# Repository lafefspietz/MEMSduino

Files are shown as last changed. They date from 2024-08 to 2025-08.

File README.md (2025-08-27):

# [MEMSduino: Arduino-Based Controller for MEMS Switches](https://github.com/lafefspietz/MEMSduino/)

## [files.html](files.html)

## [NIST Tech note describing system](https://doi.org/10.6028/NIST.TN.2335)
## [Video demonstrating operation, Zenodo.org page](https://zenodo.org/records/14811301)
## [Video doi at Zenodo](https://doi.org/10.5281/zenodo.14811300)

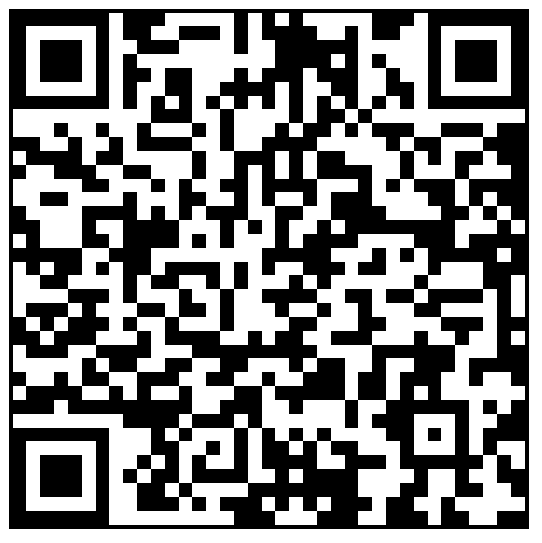
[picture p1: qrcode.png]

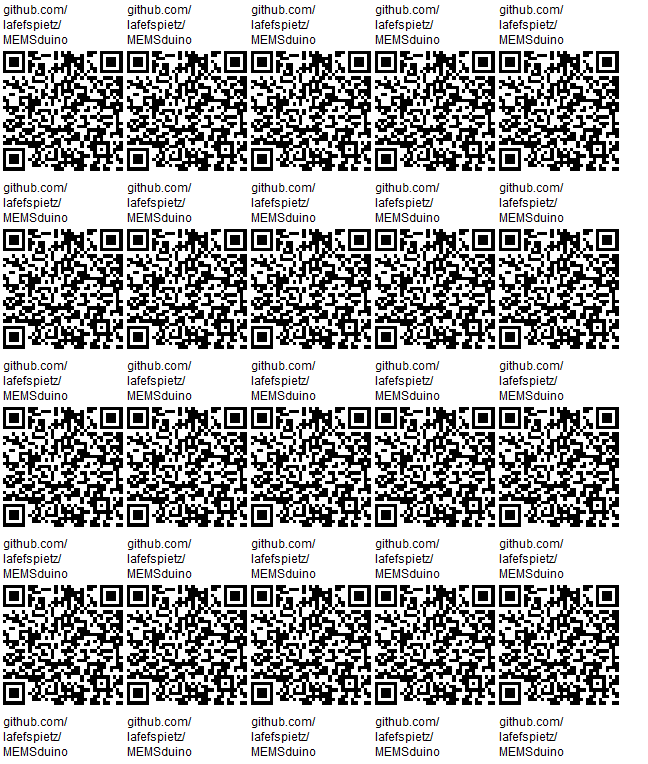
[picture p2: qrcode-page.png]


Open source system for controlling MEMS switches using an Arduino.  This system allows for both serial control via software and physical control by a human operator with buttons and indicator lights of a range of possible MEMS switch configurations.  A set of relays are controlled by the Arduino, which determines which of the lines on a DSUB connector are energized with a 90 volt signal.  This DSUB can then be connected to any cryogenic wiring which leads to the various DC control lines of a cryogenic MEMS RF switch.  

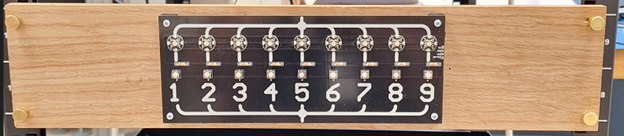
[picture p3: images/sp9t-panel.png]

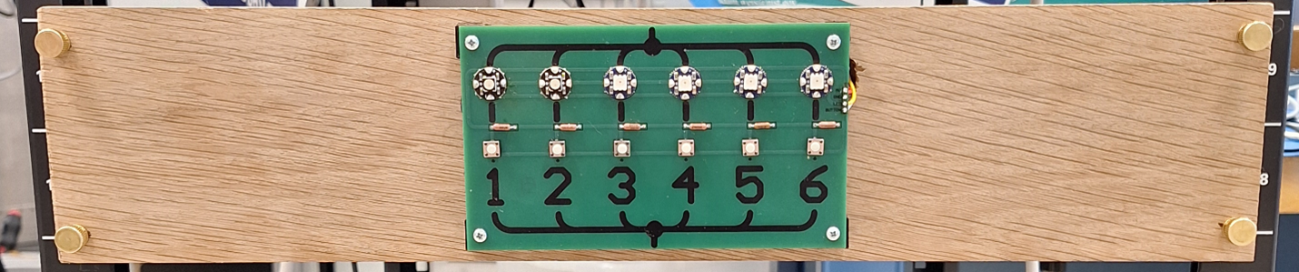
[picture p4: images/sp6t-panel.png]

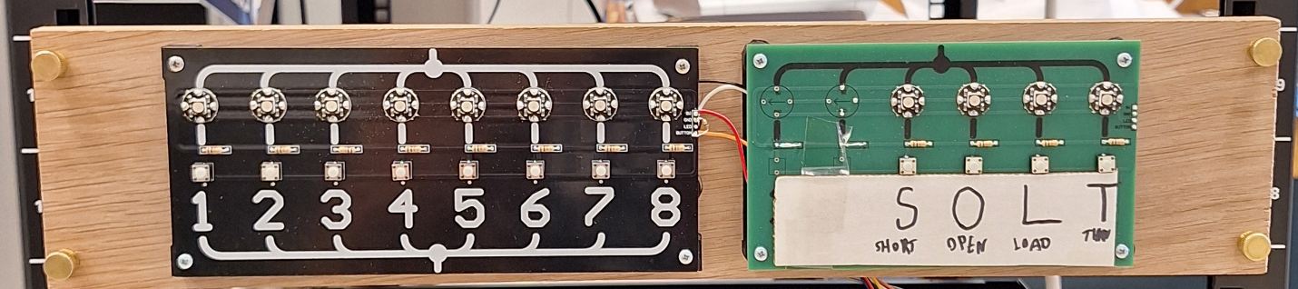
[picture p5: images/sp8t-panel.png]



## Python Code Snippets

List com port objects:
```
import serial
import serial.tools.list_ports
ports = serial.tools.list_ports.comports()

for port, desc, hwid in sorted(ports):
       print("{}: {} [{}]".format(port, desc, hwid))

```

Create serial object
```
SP9T_serial = serial.Serial('COM18', 9600)  # open serial port

```

Write to set to port 2:

```
SP9T_serial.write(bytes(str(2), encoding='utf-8'))

```

## [SP6T-COTS/](SP6T-COTS/)

## [DUAL-SP3T-COTS/](DUAL-SP3T-COTS/)

## [SP9T/](SP9T/)

## [DUAL-SP3T-COTS-SINGLE-DCDC/](DUAL-SP3T-COTS-SINGLE-DCDC/)

## [METAL BOX](metal-box/)

## [arXiv preprint DOI](https://arxiv.org/abs/2501.03340)

## All Files

 - [6_port_controller.ino](https://github.com/lafefspietz/MEMSduino/raw/refs/heads/main/6_port_controller.ino)
 - [6button-6eopixel.SchDoc](https://github.com/lafefspietz/MEMSduino/raw/refs/heads/main/6button-6eopixel.SchDoc)
 - [6button-6neopixel-BOM.xlsx](https://github.com/lafefspietz/MEMSduino/raw/refs/heads/main/6button-6neopixel-BOM.xlsx)
 - [6button-6neopixel-gerbers.zip](https://github.com/lafefspietz/MEMSduino/raw/refs/heads/main/6button-6neopixel-gerbers.zip)
 - [6button-6neopixel.PcbDoc](https://github.com/lafefspietz/MEMSduino/raw/refs/heads/main/6button-6neopixel.PcbDoc)
 - [6button-6neopixels.PrjPcb](https://github.com/lafefspietz/MEMSduino/raw/refs/heads/main/6button-6neopixels.PrjPcb)
 - [6button-6neopixels.PrjPcbStructure](https://github.com/lafefspietz/MEMSduino/raw/refs/heads/main/6button-6neopixels.PrjPcbStructure)
 - [9-port-controller.ino](https://github.com/lafefspietz/MEMSduino/raw/refs/heads/main/9-port-controller.ino)
 - [9button-9neopixel-BOM.xlsx](https://github.com/lafefspietz/MEMSduino/raw/refs/heads/main/9button-9neopixel-BOM.xlsx)
 - [9button-9neopixel-gerbers.zip](https://github.com/lafefspietz/MEMSduino/raw/refs/heads/main/9button-9neopixel-gerbers.zip)
 - [9button-9neopixel.PcbDoc](https://github.com/lafefspietz/MEMSduino/raw/refs/heads/main/9button-9neopixel.PcbDoc)
 - [9button-9neopixel.SchDoc](https://github.com/lafefspietz/MEMSduino/raw/refs/heads/main/9button-9neopixel.SchDoc)
 - [9button-9neopixels.PrjPcb](https://github.com/lafefspietz/MEMSduino/raw/refs/heads/main/9button-9neopixels.PrjPcb)
 - [9button-9neopixels.PrjPcbStructure](https://github.com/lafefspietz/MEMSduino/raw/refs/heads/main/9button-9neopixels.PrjPcbStructure)
 - [AN-1304-A-box-modifications.SLDDRW](https://github.com/lafefspietz/MEMSduino/raw/refs/heads/main/AN-1304-A-box-modifications.SLDDRW)
 - [AN-1304-A-box-modifications.SLDPRT](https://github.com/lafefspietz/MEMSduino/raw/refs/heads/main/AN-1304-A-box-modifications.SLDPRT)
 - [AN-1304-A-box-modifications.STEP](https://github.com/lafefspietz/MEMSduino/raw/refs/heads/main/AN-1304-A-box-modifications.STEP)
 - [AN-1304-A-box-modifications.pdf](https://github.com/lafefspietz/MEMSduino/raw/refs/heads/main/AN-1304-A-box-modifications.pdf)
 - [AN-1304-A-lid-modifications.SLDDRW](https://github.com/lafefspietz/MEMSduino/raw/refs/heads/main/AN-1304-A-lid-modifications.SLDDRW)
 - [AN-1304-A-lid-modifications.SLDPRT](https://github.com/lafefspietz/MEMSduino/raw/refs/heads/main/AN-1304-A-lid-modifications.SLDPRT)
 - [AN-1304-A-lid-modifications.STEP](https://github.com/lafefspietz/MEMSduino/raw/refs/heads/main/AN-1304-A-lid-modifications.STEP)
 - [AN-1304-A-lid-modifications.pdf](https://github.com/lafefspietz/MEMSduino/raw/refs/heads/main/AN-1304-A-lid-modifications.pdf)
 - [DB25-relay-HV-control-BOM.xlsx](https://github.com/lafefspietz/MEMSduino/raw/refs/heads/main/DB25-relay-HV-control-BOM.xlsx)
 - [DB25-relay-HV-control-gerbers.zip](https://github.com/lafefspietz/MEMSduino/raw/refs/heads/main/DB25-relay-HV-control-gerbers.zip)
 - [DB25-relay-HV-control.PcbDoc](https://github.com/lafefspietz/MEMSduino/raw/refs/heads/main/DB25-relay-HV-control.PcbDoc)
 - [DB25-relay-HV-control.PrjPcb](https://github.com/lafefspietz/MEMSduino/raw/refs/heads/main/DB25-relay-HV-control.PrjPcb)
 - [DB25-relay-HV-control.PrjPcbStructure](https://github.com/lafefspietz/MEMSduino/raw/refs/heads/main/DB25-relay-HV-control.PrjPcbStructure)
 - [DB25-relay-HV-control.SchDoc](https://github.com/lafefspietz/MEMSduino/raw/refs/heads/main/DB25-relay-HV-control.SchDoc)
 - [HV-DCDC-bracket.SLDDRW](https://github.com/lafefspietz/MEMSduino/raw/refs/heads/main/HV-DCDC-bracket.SLDDRW)
 - [HV-DCDC-bracket.SLDPRT](https://github.com/lafefspietz/MEMSduino/raw/refs/heads/main/HV-DCDC-bracket.SLDPRT)
 - [HV-DCDC-bracket.STL](https://github.com/lafefspietz/MEMSduino/raw/refs/heads/main/HV-DCDC-bracket.STL)
 - [HV-DCDC-bracket.pdf](https://github.com/lafefspietz/MEMSduino/raw/refs/heads/main/HV-DCDC-bracket.pdf)
 - [SP6T-COTS-BOM.xlsx](https://github.com/lafefspietz/MEMSduino/raw/refs/heads/main/SP6T-COTS-BOM.xlsx)
 - [SP9T-Custom-BOM.xlsx](https://github.com/lafefspietz/MEMSduino/raw/refs/heads/main/SP9T-Custom-BOM.xlsx)
 - [arduino-bracket.SLDDRW](https://github.com/lafefspietz/MEMSduino/raw/refs/heads/main/arduino-bracket.SLDDRW)
 - [arduino-bracket.SLDPRT](https://github.com/lafefspietz/MEMSduino/raw/refs/heads/main/arduino-bracket.SLDPRT)
 - [arduino-bracket.STL](https://github.com/lafefspietz/MEMSduino/raw/refs/heads/main/arduino-bracket.STL)
 - [arduino-bracket.pdf](https://github.com/lafefspietz/MEMSduino/raw/refs/heads/main/arduino-bracket.pdf)
 - [arduino-to-headers-shield-BOM.xlsx](https://github.com/lafefspietz/MEMSduino/raw/refs/heads/main/arduino-to-headers-shield-BOM.xlsx)
 - [arduino-to-headers-shield-gerbers.zip](https://github.com/lafefspietz/MEMSduino/raw/refs/heads/main/arduino-to-headers-shield-gerbers.zip)
 - [arduino-to-headers-shield.PcbDoc](https://github.com/lafefspietz/MEMSduino/raw/refs/heads/main/arduino-to-headers-shield.PcbDoc)
 - [arduino-to-headers-shield.PrjPcb](https://github.com/lafefspietz/MEMSduino/raw/refs/heads/main/arduino-to-headers-shield.PrjPcb)
 - [arduino-to-headers-shield.PrjPcbStructure](https://github.com/lafefspietz/MEMSduino/raw/refs/heads/main/arduino-to-headers-shield.PrjPcbStructure)
 - [arduino-to-headers-shield.SchDoc](https://github.com/lafefspietz/MEMSduino/raw/refs/heads/main/arduino-to-headers-shield.SchDoc)
 - [cryoelec-bracket.SLDDRW](https://github.com/lafefspietz/MEMSduino/raw/refs/heads/main/cryoelec-bracket.SLDDRW)
 - [cryoelec-bracket.SLDPRT](https://github.com/lafefspietz/MEMSduino/raw/refs/heads/main/cryoelec-bracket.SLDPRT)
 - [cryoelec-bracket.STL](https://github.com/lafefspietz/MEMSduino/raw/refs/heads/main/cryoelec-bracket.STL)
 - [cryoelec-bracket.pdf](https://github.com/lafefspietz/MEMSduino/raw/refs/heads/main/cryoelec-bracket.pdf)
 - [front-panel-center-bracket.SLDDRW](https://github.com/lafefspietz/MEMSduino/raw/refs/heads/main/front-panel-center-bracket.SLDDRW)
 - [front-panel-center-bracket.SLDPRT](https://github.com/lafefspietz/MEMSduino/raw/refs/heads/main/front-panel-center-bracket.SLDPRT)
 - [front-panel-center-bracket.STL](https://github.com/lafefspietz/MEMSduino/raw/refs/heads/main/front-panel-center-bracket.STL)
 - [front-panel-center-bracket.pdf](https://github.com/lafefspietz/MEMSduino/raw/refs/heads/main/front-panel-center-bracket.pdf)
 - [front-panel-edge-bracket.SLDDRW](https://github.com/lafefspietz/MEMSduino/raw/refs/heads/main/front-panel-edge-bracket.SLDDRW)
 - [front-panel-edge-bracket.SLDPRT](https://github.com/lafefspietz/MEMSduino/raw/refs/heads/main/front-panel-edge-bracket.SLDPRT)
 - [front-panel-edge-bracket.STL](https://github.com/lafefspietz/MEMSduino/raw/refs/heads/main/front-panel-edge-bracket.STL)
 - [front-panel-edge-bracket.pdf](https://github.com/lafefspietz/MEMSduino/raw/refs/heads/main/front-panel-edge-bracket.pdf)
 - [rack-mount-board-SP6T.SLDDRW](https://github.com/lafefspietz/MEMSduino/raw/refs/heads/main/rack-mount-board-SP6T.SLDDRW)
 - [rack-mount-board-SP6T.SLDPRT](https://github.com/lafefspietz/MEMSduino/raw/refs/heads/main/rack-mount-board-SP6T.SLDPRT)
 - [rack-mount-board-SP6T.pdf](https://github.com/lafefspietz/MEMSduino/raw/refs/heads/main/rack-mount-board-SP6T.pdf)
 - [rack-mount-board-SP9T.SLDDRW](https://github.com/lafefspietz/MEMSduino/raw/refs/heads/main/rack-mount-board-SP9T.SLDDRW)
 - [rack-mount-board-SP9T.SLDPRT](https://github.com/lafefspietz/MEMSduino/raw/refs/heads/main/rack-mount-board-SP9T.SLDPRT)
 - [rack-mount-board-SP9T.pdf](https://github.com/lafefspietz/MEMSduino/raw/refs/heads/main/rack-mount-board-SP9T.pdf)
 - [switch_control_matlab.m](https://github.com/lafefspietz/MEMSduino/raw/refs/heads/main/switch_control_matlab.m)
 - [switch_control_python.py](https://github.com/lafefspietz/MEMSduino/raw/refs/heads/main/switch_control_python.py)

## SP6T BOM

 - [1/2" White oak board, 4" x 24"](https://ocoochhardwoods.com/detail/?i=124wo)
 - [Brass Flared-Collar Knurled-Head Thumb Screws 10-32 Thread Size, 3/4" Long](https://www.mcmaster.com/92421A645/)
 - [#6 wood screws](https://www.amazon.com/Stainless-Phillips-Screws-Multipurpose-TPOHH/dp/B0CHRWGT8N)
 - [cryoelec-bracket](https://github.com/lafefspietz/MEMSduino/raw/refs/heads/main/cryoelec-bracket.STL)
 - [arduino-bracket](https://github.com/lafefspietz/MEMSduino/raw/refs/heads/main/arduino-bracket.STL)
 - [front-panel-edge-bracket](https://github.com/lafefspietz/MEMSduino/raw/refs/heads/main/front-panel-edge-bracket.STL)
 - [Brass threaded inserts #4-40](https://www.3djake.com/ruthex/threaded-insert-4-40-unc-100-pieces)
 - [0-80 Brass Thread Inserts(E-Z LOK 240-000-BR)](https://www.amazon.com/Z-LOK-Threaded-Insert-Plastic/dp/B08QJJDCW1/)
 - [0-80 screws  3/16" phillips, stainless](https://www.amazon.com/Machine-Screws-Phillips-Stainless-Steel/dp/B07X8NTTB9/)
 - [Zinc-Plated Steel Pan Head Phillips Screw 4-40 Thread, 1/4" Long](https://www.mcmaster.com/90272A106/)
 - [Diecast aluminum enclosure, AN-1304-A from BUD Industries](https://www.digikey.com/en/products/detail/bud-industries/AN-1304-A/5804538)
 - [Male-Female Threaded Hex Standoff 18-8 Stainless Steel, 3/16" Hex, 7/32" Long, 4-40 to 4-40 Thread](https://www.mcmaster.com/91075A462/)
 - [Brass Socket Head Screw 4-40 Thread Size, 3/4" Long](https://www.mcmaster.com/93465A113/ )
 - [Brass Washer for Number 4 Screw Size, 0.12" ID, 0.281" OD](https://www.mcmaster.com/92916A320/)
 - [6button-6neopixel, 152.4 mm x 88.9 mm (6""x3.5")](https://github.com/lafefspietz/MEMSduino/raw/refs/heads/main/6button-6neopixel-gerbers.zip)
 - [arduino-to-headers-shield 53.34 mm x 70.78 mm (2.1" x 2.79")](https://github.com/lafefspietz/MEMSduino/raw/refs/heads/main/arduino-to-headers-shield-gerbers.zip)
 - [100k axial resistor](https://www.digikey.com/en/products/detail/stackpole-electronics-inc/RNF14FTD100K/1706591)
 - [10k axial resistor](https://www.digikey.com/en/products/detail/yageo/MFR-25FBF52-10K/13219)
 - [330 ohm axial resistor](https://www.digikey.com/en/products/detail/stackpole-electronics-inc/CF18JT330R/1741683)
 - [1000 uF electrolytic capacitor](https://www.digikey.com/en/products/detail/rubycon/16PK1000MEFC10X12-5/3563556)
 - [Momentary buttons](https://www.digikey.com/en/products/detail/e-switch/TL59NF160Q/390533)
 - [JUMPER WIRE M/M 6" 20PCS](https://www.digikey.com/en/products/detail/sparkfun-electronics/PRT-12795/5993860)
 - [DB25 panel mount solder cup](https://www.digikey.com/en/products/detail/norcomp-inc/171-025-203L001/858144)
 - [Arduino UNO](https://www.digikey.com/en/products/detail/dfrobot/DFR0216/6579366)
 - [USB A to USB B cable](https://www.digikey.com/en/products/detail/assmann-wsw-components/AK672-2-2/947492)
 - [Neopixel programmable RGB LED](https://www.adafruit.com/product/1559)
 - [2 wire header cable](https://www.amazon.com/ZYAMY-Dupont-Connector-Multicolor-Breadboard/dp/B0B8Z23NWX/)
 - [4 wire header cable](https://www.amazon.com/ZYAMY-Dupont-Connector-Multicolor-Breadboard/dp/B0789F523N/)
 - [8 wire header cable](https://www.amazon.com/ZYAMY-Dupont-Connector-Multicolor-Breadboard/dp/B0789F2Y1T/ )
 - [0.1" headers](https://www.amazon.com/Header-Lystaii-Pin-Connector-Electronic/dp/B06ZZN8L9S/)

## SP9T Build BOM

 - [1/2" White oak board, 4" x 24"](https://ocoochhardwoods.com/detail/?i=124wo)
 - [Brass Flared-Collar Knurled-Head Thumb Screws 10-32 Thread Size, 3/4"" Long](https://www.mcmaster.com/92421A645/)
 - [#6 wood screws](https://www.amazon.com/Stainless-Phillips-Screws-Multipurpose-TPOHH/dp/B0CHRWGT8N)
 - [HV-DCDC-bracket.STL 3d print(4 g of filament, 14 minutes print time)](https://github.com/lafefspietz/MEMSduino/raw/refs/heads/main/HV-DCDC-bracket.STL)
 - [arduino-bracket.STL 3d print(4 g of filament, 17 minutes print time)](https://github.com/lafefspietz/MEMSduino/raw/refs/heads/main/arduino-bracket.STL)
 - [front-panel-edge-bracket.STL 3d print (3 g of filament, 14 minutes print time)](https://github.com/lafefspietz/MEMSduino/raw/refs/heads/main/front-panel-edge-bracket.STL)
 - [front-panel-center-bracket 3d print (1 g of filament, 7 minutes print time)](https://github.com/lafefspietz/MEMSduino/raw/refs/heads/main/front-panel-center-bracket.STL)
 - [Brass threaded inserts #4-40](https://www.3djake.com/ruthex/threaded-insert-4-40-unc-100-pieces)
 - [Zinc-Plated Steel Pan Head Phillips Screw 4-40 Thread, 1/4" Long](https://www.mcmaster.com/90272A106/)
 - [Diecast aluminum enclosure, AN-1304-A from BUD Industries](https://www.digikey.com/en/products/detail/bud-industries/AN-1304-A/5804538)
 - [Male-Female Threaded Hex Standoff 18-8 Stainless Steel, 3/16" Hex, 7/32" Long, 4-40 to 4-40 Thread](https://www.mcmaster.com/91075A462/)
 - [Brass Socket Head Screw 4-40 Thread Size, 3/4"" Long"](https://www.mcmaster.com/93465A113/ )
 - [Brass Washer for Number 4 Screw Size, 0.12" ID, 0.281" OD](https://www.mcmaster.com/92916A320/)
 - [5V-12V boost](https://www.amazon.com/KUNCAN-Converter-Cable-Voltage-Connector/dp/B01ID90K4A/?th=1)
 - [12V to HV boost](https://www.amazon.com/Voltage-Converter-Vintage-Indicator-80V-380V/dp/B09D93QNYK)
 - [heat shrink tubing](https://www.digikey.com/en/products/detail/3m/SFTW203-1-16-BL-SPL/22044171)
 - [9button-9neopixel 228.6mm x 88.9mm (9" x 3.5") printed circuit board](https://github.com/lafefspietz/MEMSduino/raw/refs/heads/main/9button-9neopixel-gerbers.zip)
 - [arduino-to-headers-shield 53.34 mm x 70.78 mm (2.1" x 2.79") printed circuit board](https://github.com/lafefspietz/MEMSduino/raw/refs/heads/main/arduino-to-headers-shield-gerbers.zip)
 - [DB25-relay-HV-control 78.74 mm x 71.12 mm (3.1"x2.8") printed circuit board](https://github.com/lafefspietz/MEMSduino/raw/refs/heads/main/DB25-relay-HV-control-gerbers.zip)
 - [100k axial resistor](https://www.digikey.com/en/products/detail/stackpole-electronics-inc/RNF14FTD100K/1706591)
 - [10k axial resistor](https://www.digikey.com/en/products/detail/yageo/MFR-25FBF52-10K/13219)
 - [330 ohm axial resistor](https://www.digikey.com/en/products/detail/stackpole-electronics-inc/CF18JT330R/1741683)
 - [1000 uF electrolytic capacitor](https://www.digikey.com/en/products/detail/rubycon/16PK1000MEFC10X12-5/3563556)
 - [Momentary buttons](https://www.digikey.com/en/products/detail/e-switch/TL59NF160Q/390533)
 - [1 Mohm 1206 SMT resistor 1%](https://www.digikey.com/en/products/detail/yageo/RC1206FR-071ML/728388)
 - [DB25 board mount connector](https://www.digikey.com/en/products/detail/assmann-wsw-components/A-DF-25-PP-Z/1241794)
 - [RELAY REED SIP SPST .5A 5V W/DIO](https://www.digikey.com/en/products/detail/comus-international/3570-1331-053/7497099)
 - [Arduino UNO](https://www.digikey.com/en/products/detail/dfrobot/DFR0216/6579366)
 - [USB A to USB B cable](https://www.digikey.com/en/products/detail/assmann-wsw-components/AK672-2-2/947492)
 - [Neopixel programmable RGB LED](https://www.adafruit.com/product/1559)
 - [2 wire header cable](https://www.amazon.com/ZYAMY-Dupont-Connector-Multicolor-Breadboard/dp/B0B8Z23NWX/)
 - [4 wire header cable](https://www.amazon.com/ZYAMY-Dupont-Connector-Multicolor-Breadboard/dp/B0789F523N/)
 - [8 wire header cable](https://www.amazon.com/ZYAMY-Dupont-Connector-Multicolor-Breadboard/dp/B0789F2Y1T/ )
 - [0.1" headers](https://www.amazon.com/Header-Lystaii-Pin-Connector-Electronic/dp/B06ZZN8L9S/)

## Disclaimer

Certain equipment, instruments, software, or materials are identified in this document in order to specify the experimental procedure adequately.  Such identification is not intended to imply recommendation or endorsement of any product or service by NIST, nor is it intended to imply that the materials or equipment identified are necessarily the best available for the purpose.

## MEMSduino SP9T Build Sequence

1. Cut wood board and drill holes in it
2. Cut out holes and D Sub Cutout in BUD box, mount DSUB into D cutout with 4-40 standoffs, mount to wood with long 4-40 screws
3. 3d print all 3d printed parts and add heat-pressed thread inserts
4. Screw all brackets to the wood board except for the HV-DCDC-bracket.STL, which is screwed to the inside of the BUD box.
5. Assemble Arduino UNO Shield board (arduino-to-headers-shield)
6. Mount the Arduino UNO to the 3d printed Arduino mounting bracket with 4-40 screws and plug the shield into the UNO
6. Assemble Relay control board (DB25-relay-HV-control), solder to captive DSUB connector in the lid of BUD box
7. Assemble the DC DC converter as needed to get to 90 volts or install an off the shelf converter in the BUD box, mount the board to the board mount bracket.
8. Assemble front panel control circuit board, mount it to the plastic brackets on the wood board
9. Connect all the cables, test system

## MEMSduino SP6T COTS Build Sequence

1. Cut wood board and drill holes in it
2. Cut out holes and D Sub Cutout in BUD box, mount DSUB into D cutout with 4-40 standoffs, mount to wood with long 4-40 screws
3. 3d print all 3d printed parts and add heat-pressed thread inserts, 4-40 on all but cryoelec-bracket, which takes 0-80 thread inserts
4. Screw all brackets to the wood board except for the cryoelec-bracket.STL part, which is screwed to the inside of the BUD box with 4-40 screws
5. Assemble Arduino UNO Shield board (arduino-to-headers-shield)
6. Mount the Arduino UNO to the 3d printed Arduino mounting bracket with 4-40 screws and plug the shield into the UNO
7. Put male header pins in the input side of the DC DC converter, and the jumper wires in the output side, mount board in metal box with 0-80 screws, connect to the Arduino shield with one 8 wire cable and one 4 wire cable, making sure all pins map in order.
8. Solder the ends of the jumper wires into the solder cups in the DSUB connector, matching with whatever pins map to the appropriate pins on the cryogenic SP6T COTS switch
8. Assemble front panel control circuit board, mount it to the plastic brackets on the wood board
9. Connect all the cables, test system

## License

This data/work was created by employees of the National Institute of Standards and Technology (NIST), an agency of the Federal Government. Pursuant to title 17 United States Code Section 105, works of NIST employees are not subject to copyright protection in the United States.  This data/work may be subject to foreign copyright.

The data/work is provided by NIST as a public service and is expressly provided “AS IS.” NIST MAKES NO WARRANTY OF ANY KIND, EXPRESS, IMPLIED OR STATUTORY, INCLUDING, WITHOUT LIMITATION, THE IMPLIED WARRANTY OF MERCHANTABILITY, FITNESS FOR A PARTICULAR PURPOSE, NON-INFRINGEMENT AND DATA ACCURACY. NIST does not warrant or make any representations regarding the use of the data or the results thereof, including but not limited to the correctness, accuracy, reliability or usefulness of the data. NIST SHALL NOT BE LIABLE AND YOU HEREBY RELEASE NIST FROM LIABILITY FOR ANY INDIRECT, CONSEQUENTIAL, SPECIAL, OR INCIDENTAL DAMAGES (INCLUDING DAMAGES FOR LOSS OF BUSINESS PROFITS, BUSINESS INTERRUPTION, LOSS OF BUSINESS INFORMATION, AND THE LIKE), WHETHER ARISING IN TORT, CONTRACT, OR OTHERWISE, ARISING FROM OR RELATING TO THE DATA (OR THE USE OF OR INABILITY TO USE THIS DATA), EVEN IF NIST HAS BEEN ADVISED OF THE POSSIBILITY OF SUCH DAMAGES.

To the extent that NIST may hold copyright in countries other than the United States, you are hereby granted the non-exclusive irrevocable and unconditional right to print, publish, prepare derivative works and distribute the NIST data, in any medium, or authorize others to do so on your behalf, on a royalty-free basis throughout the world.

You may improve, modify, and create derivative works of the data or any portion of the data, and you may copy and distribute such modifications or works. Modified works should carry a notice stating that you changed the data and should note the date and nature of any such change. Please explicitly acknowledge the National Institute of Standards and Technology as the source of the data:  Data citation recommendations are provided at https://www.nist.gov/open/license.

Permission to use this data is contingent upon your acceptance of the terms of this agreement and upon your providing appropriate acknowledgments of NIST’s creation of the data/work.

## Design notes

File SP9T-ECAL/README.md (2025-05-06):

# [SP9T SP4T ECAL](https://github.com/lafefspietz/MEMSduino/tree/main/SP9T-ECAL)

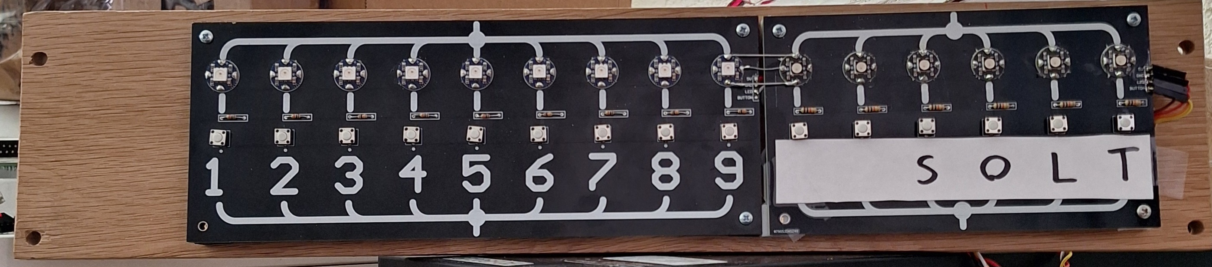
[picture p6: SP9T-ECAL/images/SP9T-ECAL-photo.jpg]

## [SP9T-ECAL.ino](https://github.com/lafefspietz/MEMSduino/blob/main/SP9T-ECAL/arduino/SP9T-ECAL/SP9T-ECAL.ino)
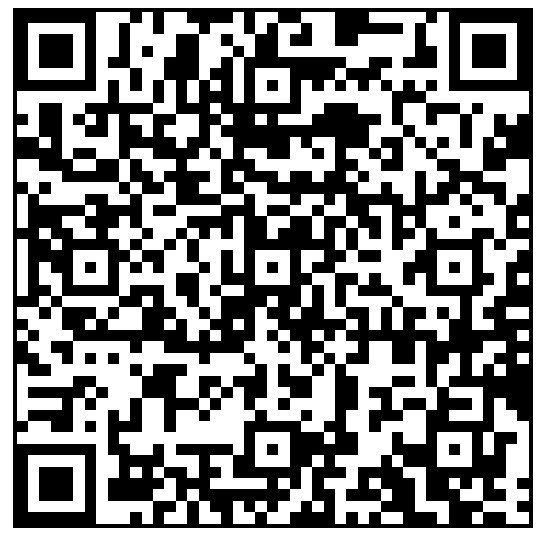
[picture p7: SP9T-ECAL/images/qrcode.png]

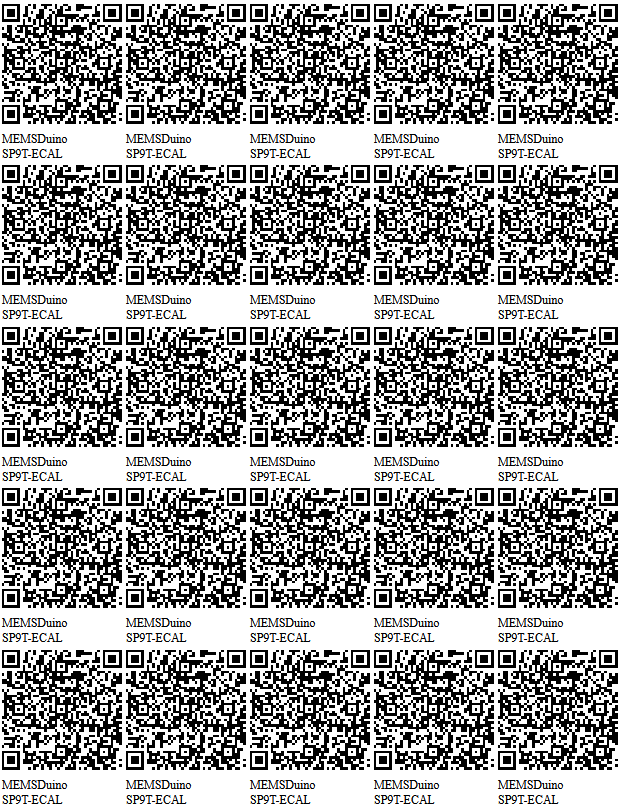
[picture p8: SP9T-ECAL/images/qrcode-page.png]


## [SP9T-ECAL.ino](https://github.com/lafefspietz/MEMSduino/blob/main/SP9T-ECAL/arduino/SP9T-ECAL/SP9T-ECAL.ino)

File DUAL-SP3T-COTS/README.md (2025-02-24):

# [Dual SP3T COTS](https://github.com/lafefspietz/MEMSduino/tree/main/DUAL-SP3T-COTS)

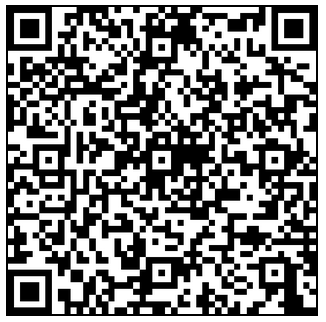
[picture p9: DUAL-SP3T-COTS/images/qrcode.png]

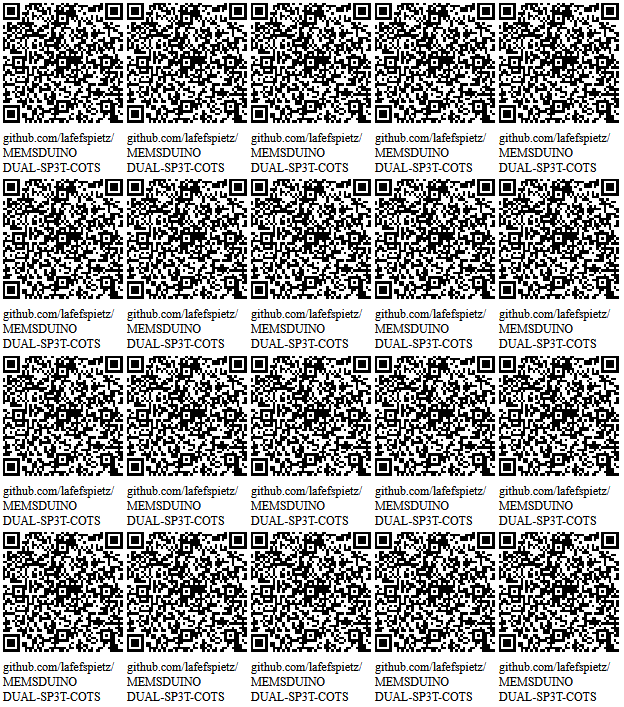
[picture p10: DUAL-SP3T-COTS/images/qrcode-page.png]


Arduino-based control panel for [3PST switches](https://www.cryoelec.com/products/cryoswitchsp3t) from [Cryo-elec](https://www.cryoelec.com/).

To program over serial, connect at 9600 baud and send the character of the number you want to select. For example to select 1, send "1".

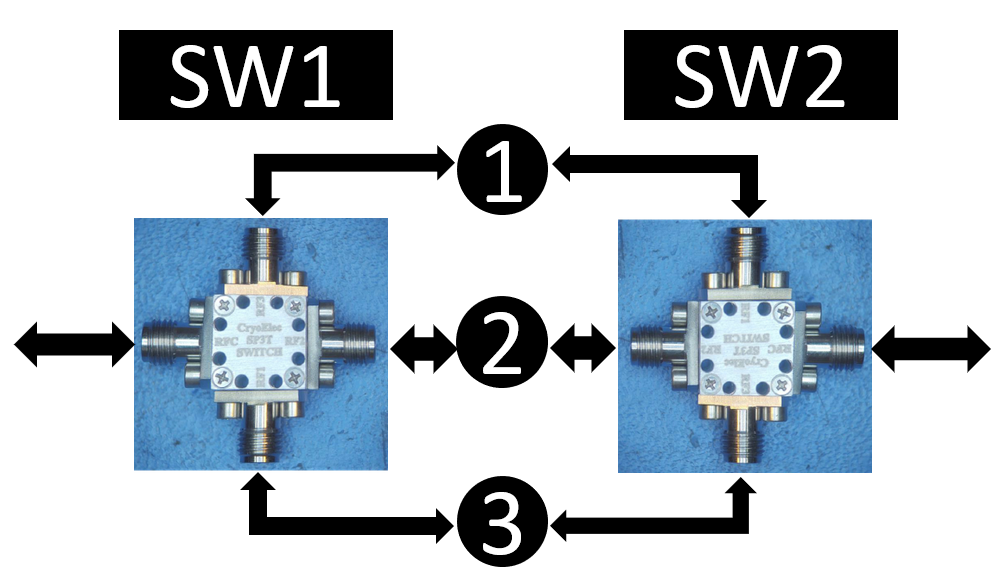
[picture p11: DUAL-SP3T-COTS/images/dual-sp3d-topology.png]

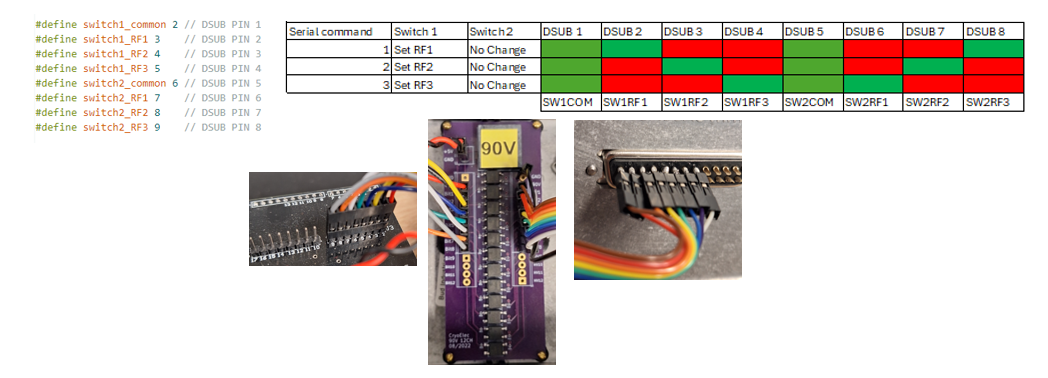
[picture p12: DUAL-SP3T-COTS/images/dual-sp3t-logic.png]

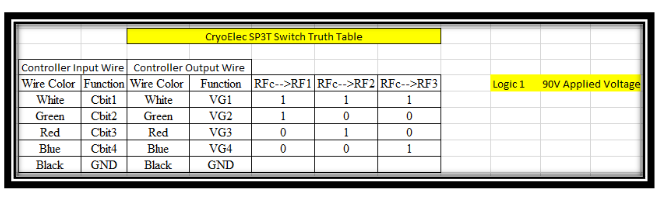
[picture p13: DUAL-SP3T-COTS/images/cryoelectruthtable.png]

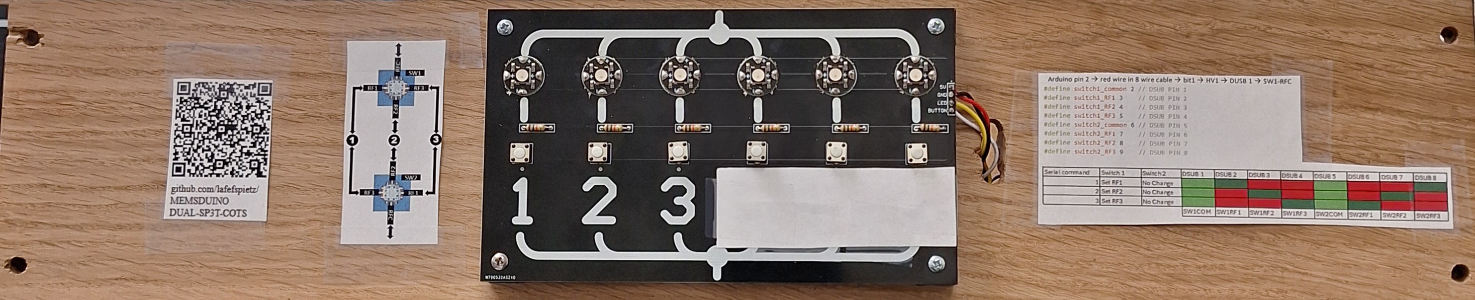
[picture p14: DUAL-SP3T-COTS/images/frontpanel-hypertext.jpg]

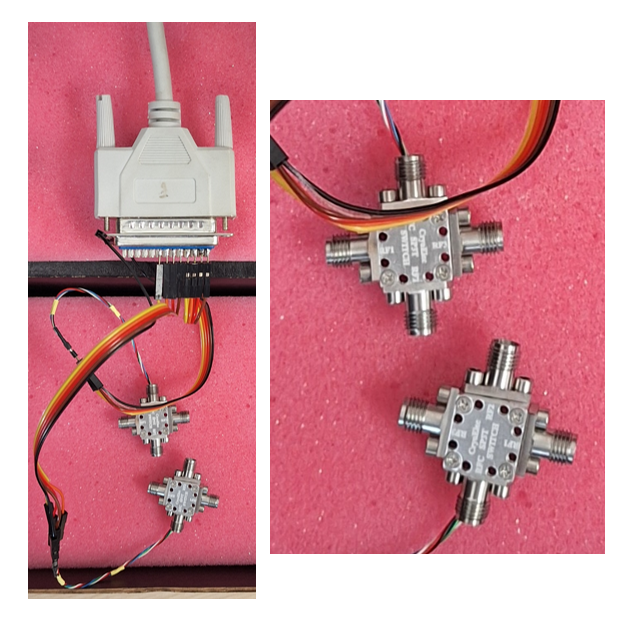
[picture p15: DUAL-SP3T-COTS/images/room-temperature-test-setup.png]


## Wood Board Fabrication and Assembly

Buy a 4 inch by 24 inch by half inch white oak board, cut down to 19 inches. Download and print out in 1:1 scale single sided the pdf linked below to 

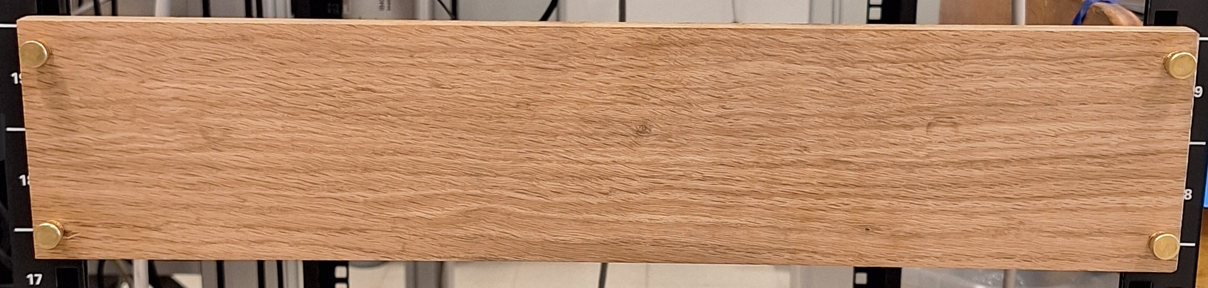
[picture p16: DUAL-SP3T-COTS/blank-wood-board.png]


[Link to buy board](https://ocoochhardwoods.com/detail/?i=124wo)

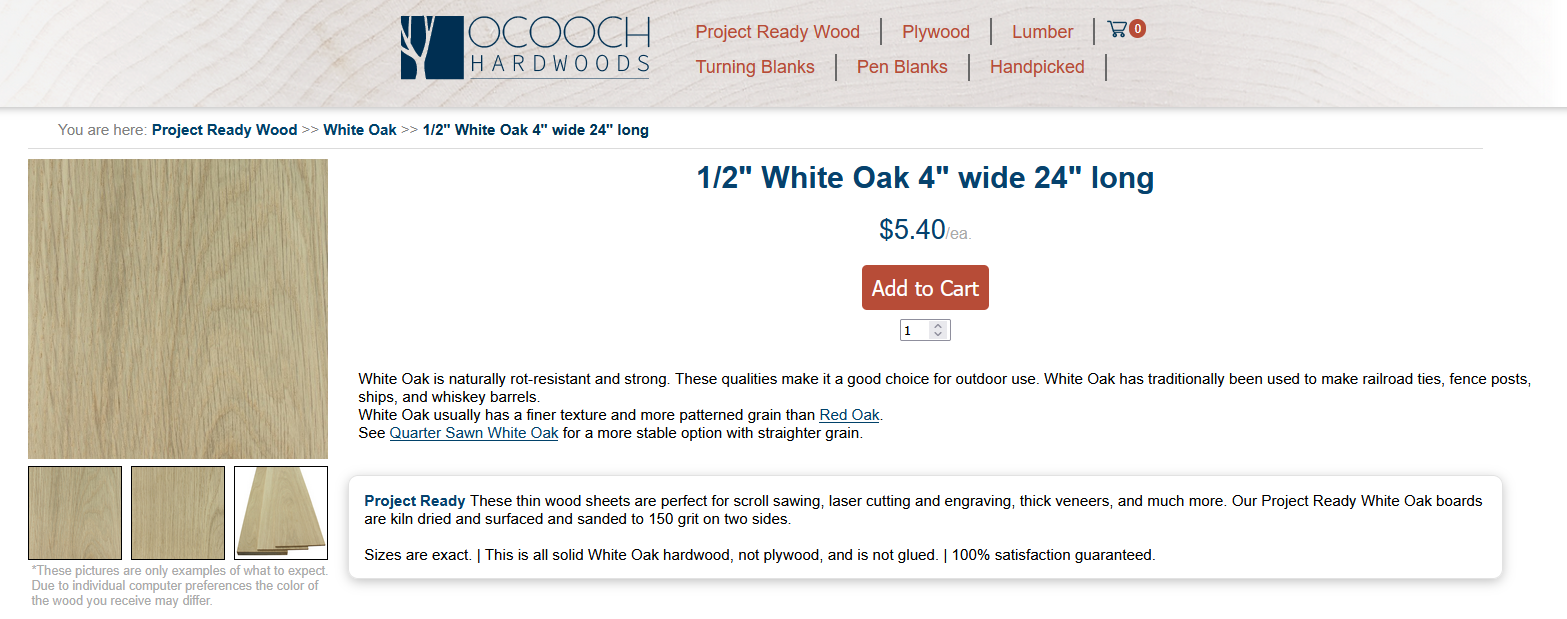
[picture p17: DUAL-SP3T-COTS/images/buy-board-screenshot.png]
(https://ocoochhardwoods.com/detail/?i=124wo)


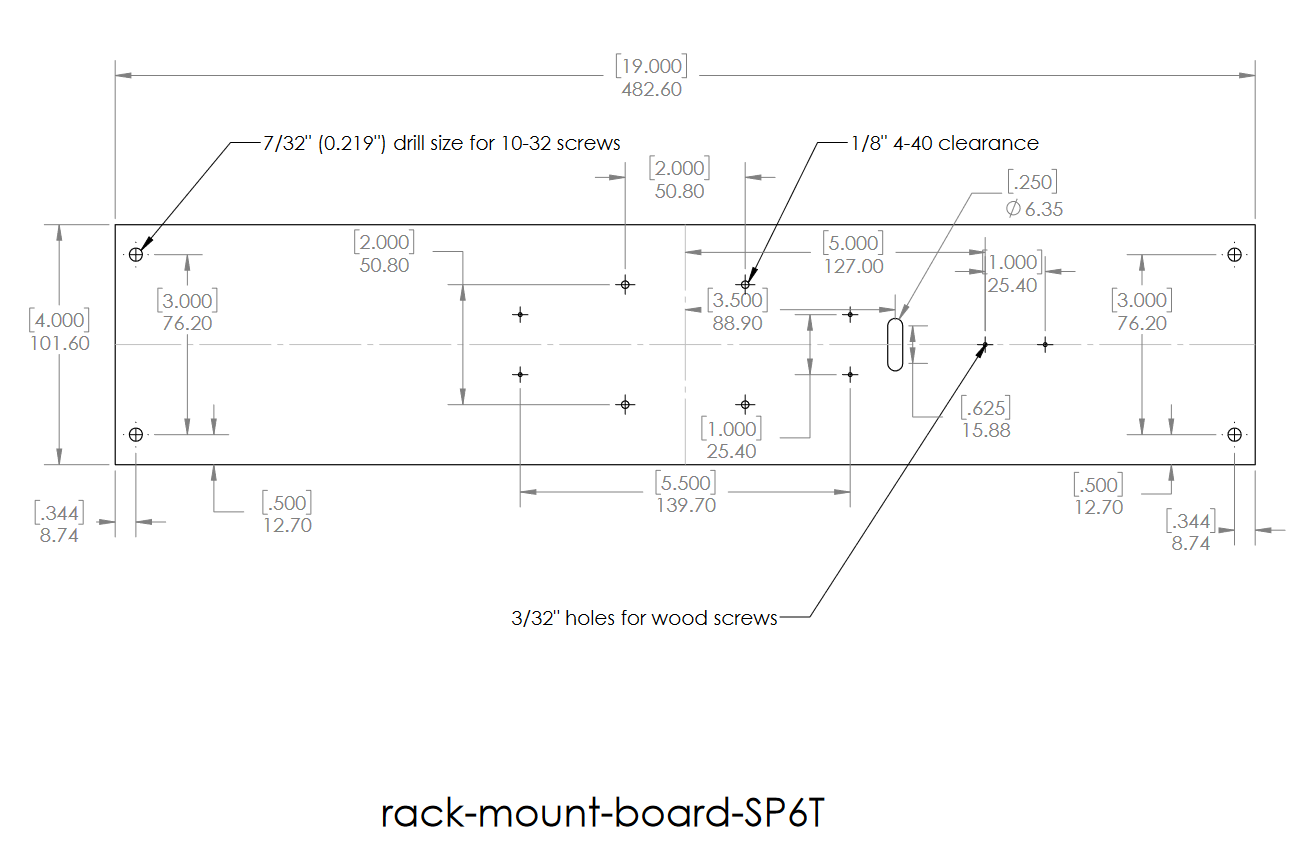
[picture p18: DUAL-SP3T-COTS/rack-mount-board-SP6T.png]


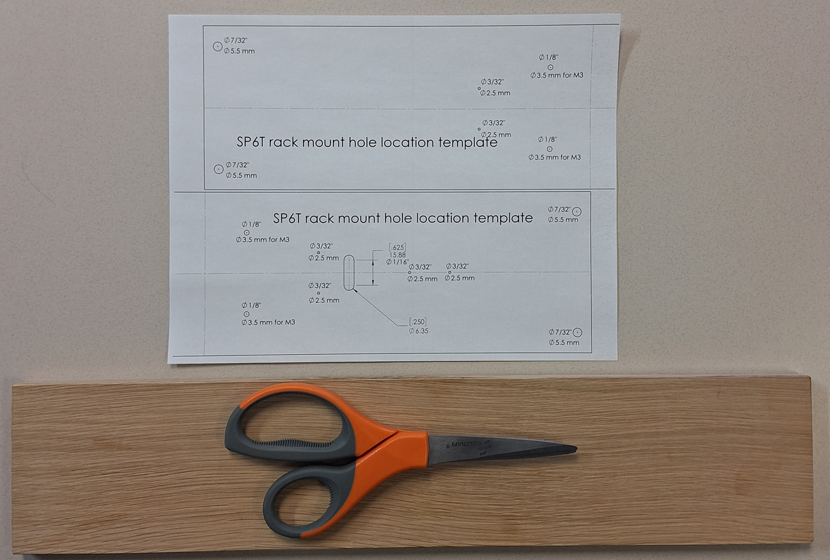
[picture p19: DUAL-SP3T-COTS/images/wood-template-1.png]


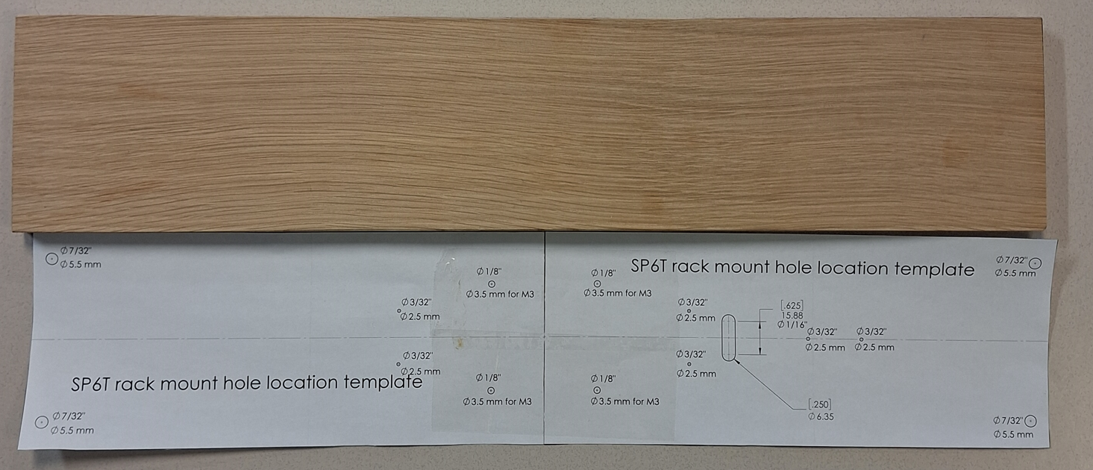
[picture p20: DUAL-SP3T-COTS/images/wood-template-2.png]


## Fasteners and Inserts

### 10-32 rack mount screws with knurled head

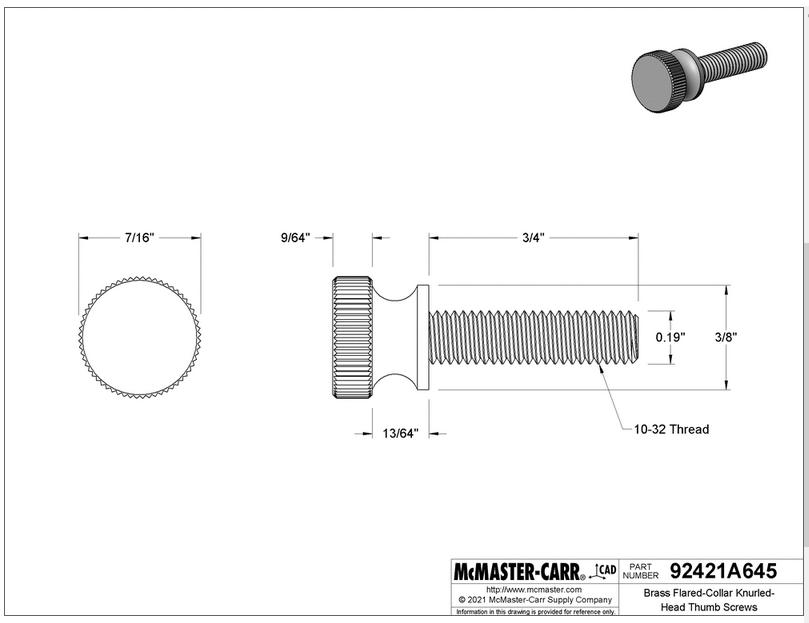
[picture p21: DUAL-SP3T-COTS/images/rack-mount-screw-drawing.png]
(https://www.mcmaster.com/92421A645/)


(https://www.mcmaster.com/92421A645/)

### #6 Wood Phillips screws

(https://www.amazon.com/Stainless-Phillips-Screws-Multipurpose-TPOHH/dp/B0CHRWGT8N)

### 0-80 Screws and Inserts

(https://www.amazon.com/Machine-Screws-Phillips-Stainless-Steel/dp/B07X8NTTB9/)

(https://www.amazon.com/Z-LOK-Threaded-Insert-Plastic/dp/B08QJJDCW1/)

### 4-40 Screws, Inserts, and Washers

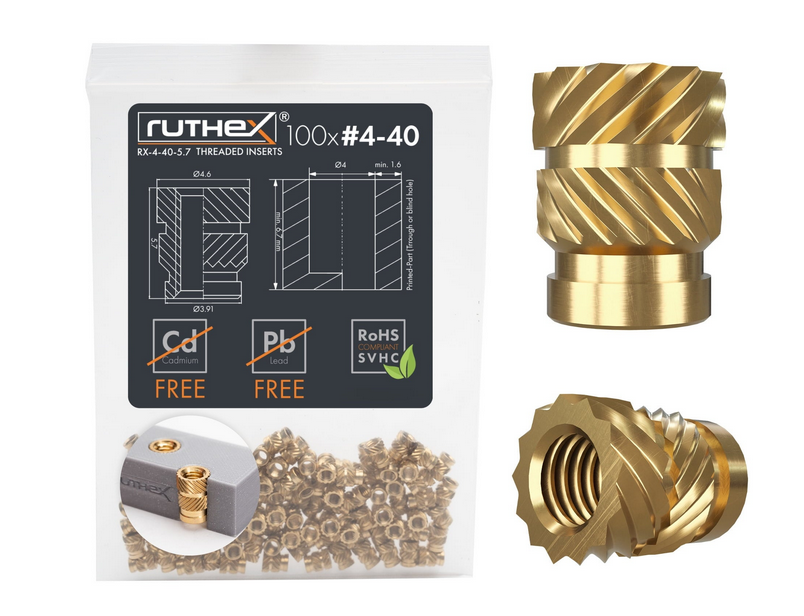
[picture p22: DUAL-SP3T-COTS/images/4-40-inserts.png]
(https://www.3djake.com/ruthex/threaded-insert-4-40-unc-100-pieces)


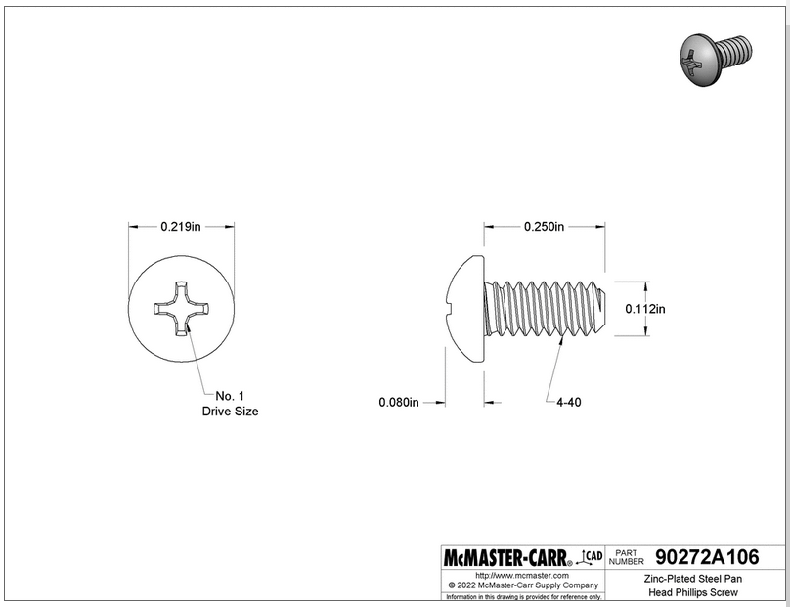
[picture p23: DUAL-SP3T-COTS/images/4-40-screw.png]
(https://www.mcmaster.com/90272A106/)

(https://www.mcmaster.com/90272A106/)

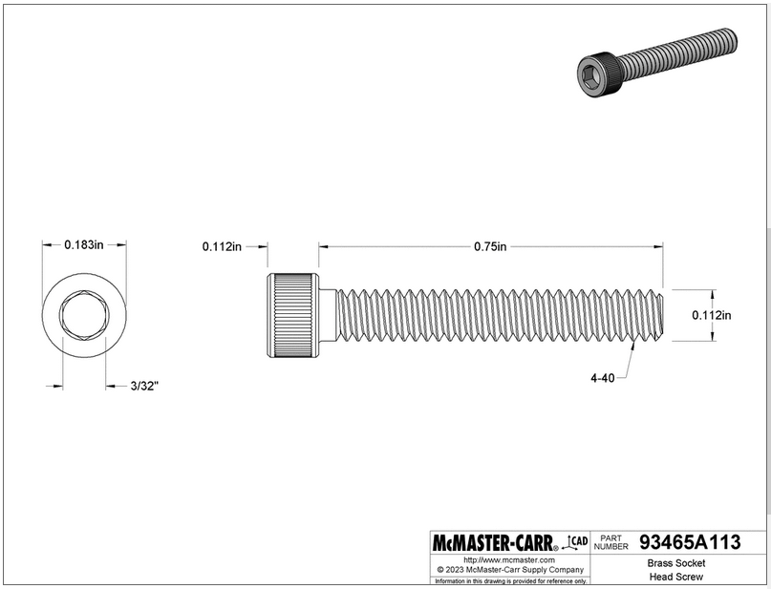
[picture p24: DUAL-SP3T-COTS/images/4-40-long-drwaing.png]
(https://www.mcmaster.com/93465A113/)

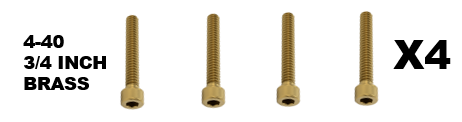
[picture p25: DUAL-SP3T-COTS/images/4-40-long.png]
(https://www.mcmaster.com/93465A113/)


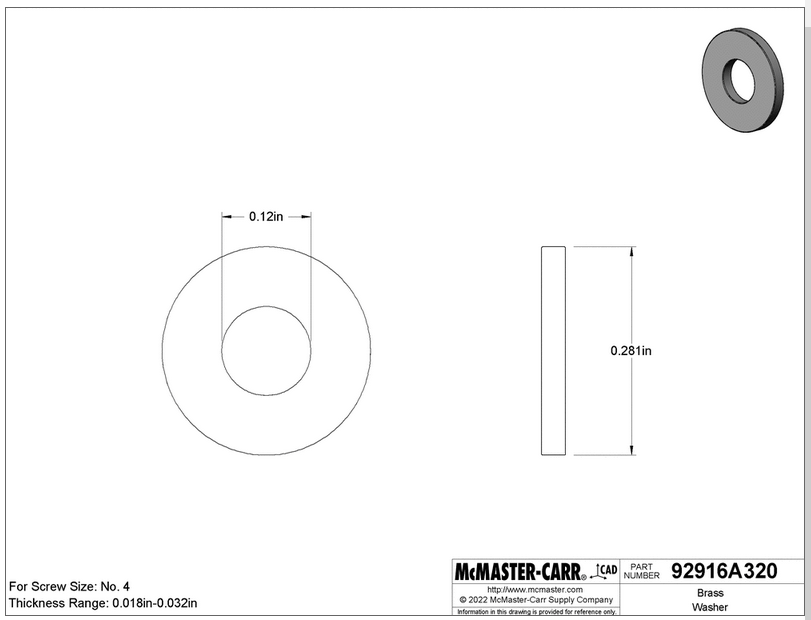
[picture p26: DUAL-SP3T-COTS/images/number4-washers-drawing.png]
(https://www.mcmaster.com/92916A320/)

(https://www.mcmaster.com/92916A320/)

## 3d Printed Brackets

### Bracket for Cryo-Elect 12 channel HV Board

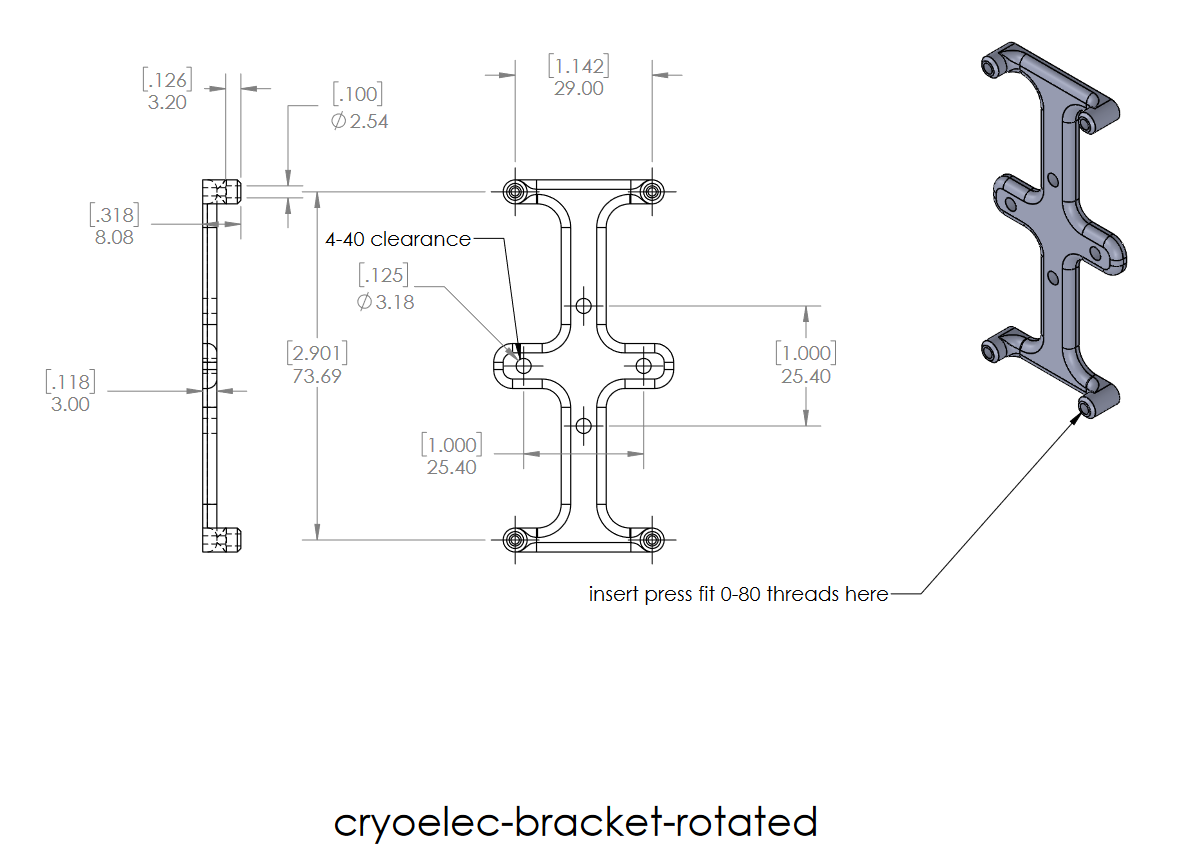
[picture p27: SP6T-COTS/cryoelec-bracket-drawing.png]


### Arduino Bracket

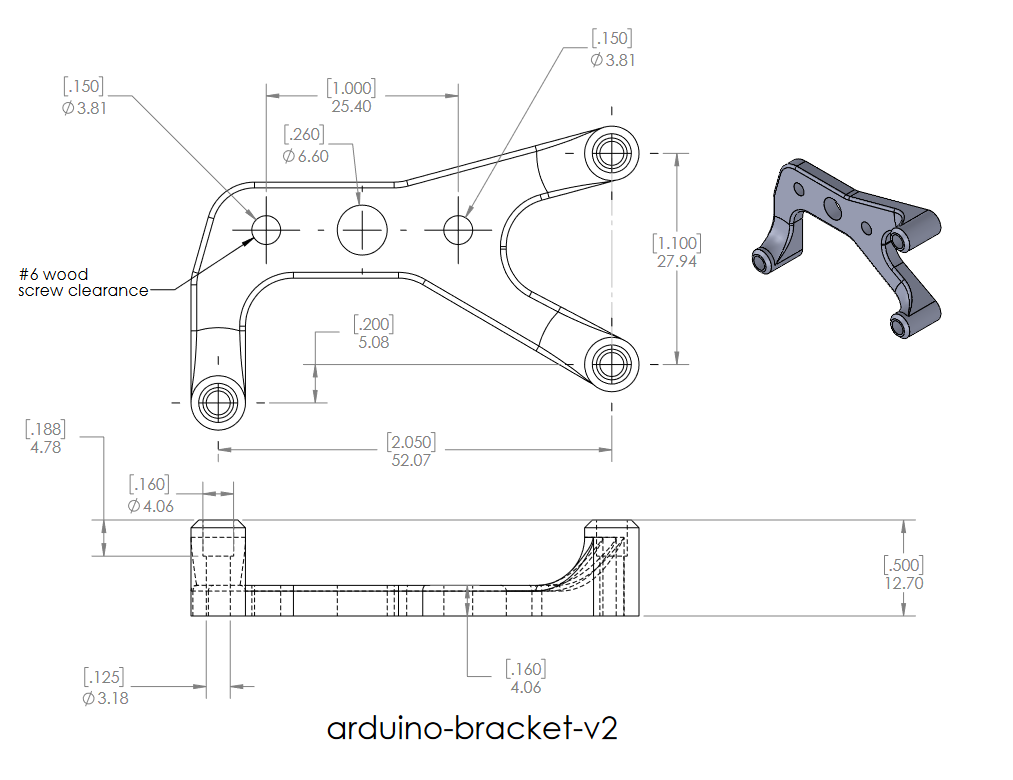
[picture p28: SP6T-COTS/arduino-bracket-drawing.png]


### Front Panel Bracket

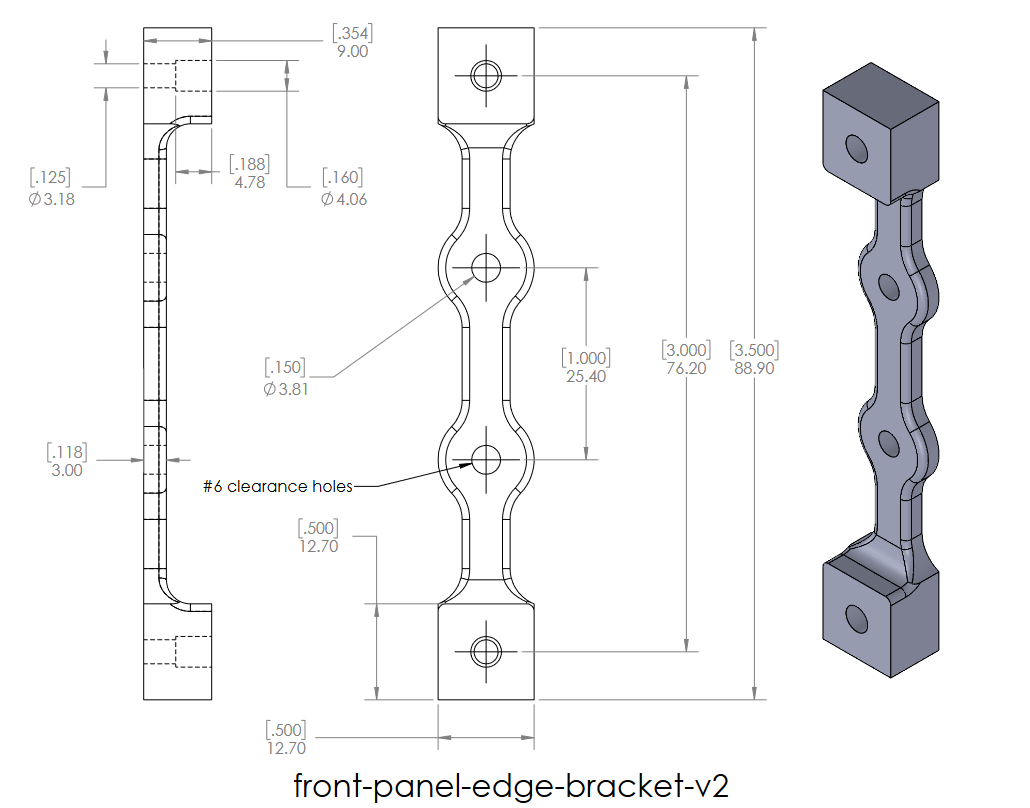
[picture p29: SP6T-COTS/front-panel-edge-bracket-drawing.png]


## Metal Box





## Circuit Boards

[SEE SP6T](https://github.com/lafefspietz/MEMSduino/tree/main/SP6T-COTS)

## BUILD GUIDE

1. Cut [1/2" thick 4" x 24" wood board](https://ocoochhardwoods.com/detail/?i=124wo) down to 19 inches wide
2. Download the template file [rack-mount-board-SP6T.pdf](https://github.com/lafefspietz/MEMSduino/blob/19722ce00cc25ea43800a57261b41cfc357cee65/rack-mount-board-SP6T.pdf) and print it out in 1:1 scale so that the dimensions are exactly correct, cut it out, and tape it together along the dotted line to form a single 19" x 4" template. Check that it is really the right size for the board.
3. Use a sharp tool to transfer hole locations from the paper template to the board, and drill holes as marked on the template. This can be done with a hand drill.
4. 3d print the plastic parts as follows:
    - [2 each of front-panel-edge-bracket.STL](https://github.com/lafefspietz/MEMSduino/raw/refs/heads/main/front-panel-edge-bracket.STL)
    - [1 of  cryoelec-bracket.STL](https://github.com/lafefspietz/MEMSduino/raw/refs/heads/main/cryoelec-bracket.STL)
    - [1 of arduino-bracket.STL](https://github.com/lafefspietz/MEMSduino/raw/refs/heads/main/arduino-bracket.STL)
5. Insert brass [4-40 brass thread inserts](https://www.3djake.com/ruthex/threaded-insert-4-40-unc-100-pieces)(7x) into Arduino bracket and front panel edge bracket with hot soldering iron
6. Insert brass [0-80 brass thread inserts](https://www.amazon.com/Z-LOK-Threaded-Insert-Plastic/dp/B08QJJDCW1/) upside down in cryo-elec bracket by simple force
7. Remove 24 pins from the [0.1" header strips](https://www.amazon.com/Header-Lystaii-Pin-Connector-Electronic/dp/B06ZZN8L9S/) and use them to solder the [Adafruit Neopixels](https://www.adafruit.com/product/1559), add the [10k resistors](https://www.digikey.com/en/products/detail/yageo/MFP-25BRD52-10K/2058797) and [buttons](https://www.digikey.com/en/products/detail/e-switch/TL59NF160Q/390533), and connect a [4 pin cable](https://www.amazon.com/ZYAMY-Dupont-Connector-Multicolor-Breadboard/dp/B0789F523N/) with one end cut and stripped to the header holes, with the red wire going to the 5v line.
8. Assemble the Arduino shield, double checking that the capacitor is not in backwards.
9. Buy an [AN-1304-A die cast aluminum enclosure](https://www.digikey.com/en/products/detail/bud-industries/AN-1304-A/5804538) from Bud Industries and have it modified using the drawings [AN-1304-A-box-modifications.pdf](https://github.com/lafefspietz/MEMSduino/raw/refs/heads/main/AN-1304-A-box-modifications.pdf) and [AN-1304-A-lid-modifications.pdf](https://github.com/lafefspietz/MEMSduino/raw/refs/heads/main/AN-1304-A-lid-modifications.pdf) and the STEP files [AN-1304-A-box-modifications.STEP](https://github.com/lafefspietz/MEMSduino/raw/refs/heads/main/AN-1304-A-box-modifications.STEP) and [AN-1304-A-lid-modifications.STEP](https://github.com/lafefspietz/MEMSduino/raw/refs/heads/main/AN-1304-A-lid-modifications.STEP). Or machine it yourself, if you have a mill.
10. Screw the Arduino bracket to one side of the wood and the two front panel brackets to the other side with the [#6 wood screws](https://www.amazon.com/Stainless-Phillips-Screws-Multipurpose-TPOHH/dp/B0CHRWGT8N). Screw the Arduino UNO to the Arduino bracket using the [1/4" #4 screws](https://www.mcmaster.com/90272A106/), as well as the front panel to the brackets on the front of the board, and insert the Arduino shield board into the sockets header strips on the Arduino.  Connect the [2 pin cable](https://www.amazon.com/ZYAMY-Dupont-Connector-Multicolor-Breadboard/dp/B0B8Z23NWX/), [4 pin cable](https://www.amazon.com/ZYAMY-Dupont-Connector-Multicolor-Breadboard/dp/B0789F523N/), and [8 pin cable](https://www.amazon.com/ZYAMY-Dupont-Connector-Multicolor-Breadboard/dp/B0789F2Y1T/ ) to the headers.
11. Insert [0.1" header strips](https://www.amazon.com/Header-Lystaii-Pin-Connector-Electronic/dp/B06ZZN8L9S/) into the input side of the DC DC boost board that comes with the SP6T switch from Cryoelec, screw them into place, and also screw into place the strip of jumpers on the output side.  Connect a [2 pin cable](https://www.amazon.com/ZYAMY-Dupont-Connector-Multicolor-Breadboard/dp/B0B8Z23NWX/), [4 pin cable](https://www.amazon.com/ZYAMY-Dupont-Connector-Multicolor-Breadboard/dp/B0789F523N/), and [8 pin cable](https://www.amazon.com/ZYAMY-Dupont-Connector-Multicolor-Breadboard/dp/B0789F2Y1T/ ) to the headers. 
12. Screw the 3d printed mounting bracket for the DC DC converter with the 0-80 thread inserts into the aluminum box with 1/4" 4-40 screws, and screw the DC DC converter board to the bracket with the [0-80 screws](https://www.amazon.com/Machine-Screws-Phillips-Stainless-Steel/dp/B07X8NTTB9/)
13. Screw the aluminum box to the wood board with the set of 4 [3/4" long 4-40 brass socket cap screws](https://www.mcmaster.com/93465A113/ ) and [washers](https://www.mcmaster.com/92916A320/).
14. Screw the [DSub solder cup connector](https://www.digikey.com/en/products/detail/norcomp-inc/171-025-103L001/858135) into the lid with the [4-40 hex standoffs](https://www.mcmaster.com/91075A462/)
15. Solder appropriate wires to socket cups for the pins on the bottom of the fridge which go to the switch.

## BILL OF MATERIALS

 - [1/2" White oak board, 4" x 24"](https://ocoochhardwoods.com/detail/?i=124wo)
 - [Brass Flared-Collar Knurled-Head Thumb Screws 10-32 Thread Size, 3/4" Long](https://www.mcmaster.com/92421A645/)
 - [#6 wood screws](https://www.amazon.com/Stainless-Phillips-Screws-Multipurpose-TPOHH/dp/B0CHRWGT8N)
 - [cryoelec-bracket](https://github.com/lafefspietz/MEMSduino/raw/refs/heads/main/cryoelec-bracket.STL)
 - [arduino-bracket](https://github.com/lafefspietz/MEMSduino/raw/refs/heads/main/arduino-bracket.STL)
 - [front-panel-edge-bracket](https://github.com/lafefspietz/MEMSduino/raw/refs/heads/main/front-panel-edge-bracket.STL)
 - [Brass threaded inserts #4-40](https://www.3djake.com/ruthex/threaded-insert-4-40-unc-100-pieces)
 - [0-80 Brass Thread Inserts(E-Z LOK 240-000-BR)](https://www.amazon.com/Z-LOK-Threaded-Insert-Plastic/dp/B08QJJDCW1/)
 - [0-80 screws  3/16" phillips, stainless](https://www.amazon.com/Machine-Screws-Phillips-Stainless-Steel/dp/B07X8NTTB9/)
 - [Zinc-Plated Steel Pan Head Phillips Screw 4-40 Thread, 1/4" Long](https://www.mcmaster.com/90272A106/)
 - [Diecast aluminum enclosure, AN-1304-A from BUD Industries](https://www.digikey.com/en/products/detail/bud-industries/AN-1304-A/5804538)
 - [Male-Female Threaded Hex Standoff 18-8 Stainless Steel, 3/16" Hex, 7/32" Long, 4-40 to 4-40 Thread](https://www.mcmaster.com/91075A462/)
 - [Brass Socket Head Screw 4-40 Thread Size, 3/4" Long](https://www.mcmaster.com/93465A113/ )
 - [Brass Washer for Number 4 Screw Size, 0.12" ID, 0.281" OD](https://www.mcmaster.com/92916A320/)
 - [6button-6neopixel, 152.4 mm x 88.9 mm (6""x3.5")](https://github.com/lafefspietz/MEMSduino/raw/refs/heads/main/6button-6neopixel-gerbers.zip)
 - [arduino-to-headers-shield 53.34 mm x 70.78 mm (2.1" x 2.79")](https://github.com/lafefspietz/MEMSduino/raw/refs/heads/main/arduino-to-headers-shield-gerbers.zip)
 - [100k axial resistor](https://www.digikey.com/en/products/detail/stackpole-electronics-inc/RNF14FTD100K/1706591)
 - [10k axial resistor](https://www.digikey.com/en/products/detail/yageo/MFR-25FBF52-10K/13219)
 - [330 ohm axial resistor](https://www.digikey.com/en/products/detail/stackpole-electronics-inc/CF18JT330R/1741683)
 - [1000 uF electrolytic capacitor](https://www.digikey.com/en/products/detail/rubycon/16PK1000MEFC10X12-5/3563556)
 - [Momentary buttons](https://www.digikey.com/en/products/detail/e-switch/TL59NF160Q/390533)
 - [JUMPER WIRE M/M 6" 20PCS](https://www.digikey.com/en/products/detail/sparkfun-electronics/PRT-12795/5993860)
 - [DB25 panel mount solder cup](https://www.digikey.com/en/products/detail/norcomp-inc/171-025-203L001/858144)
 - [Arduino UNO](https://www.digikey.com/en/products/detail/dfrobot/DFR0216/6579366)
 - [USB A to USB B cable](https://www.digikey.com/en/products/detail/assmann-wsw-components/AK672-2-2/947492)
 - [Neopixel programmable RGB LED](https://www.adafruit.com/product/1559)
 - [2 wire header cable](https://www.amazon.com/ZYAMY-Dupont-Connector-Multicolor-Breadboard/dp/B0B8Z23NWX/)
 - [4 wire header cable](https://www.amazon.com/ZYAMY-Dupont-Connector-Multicolor-Breadboard/dp/B0789F523N/)
 - [8 wire header cable](https://www.amazon.com/ZYAMY-Dupont-Connector-Multicolor-Breadboard/dp/B0789F2Y1T/ )
 - [0.1" headers](https://www.amazon.com/Header-Lystaii-Pin-Connector-Electronic/dp/B06ZZN8L9S/)

## Files

 - [cryoelec-bracket-SP3T.SLDDRW](https://github.com/lafefspietz/MEMSduino/raw/refs/heads/main/cryoelec-bracket-SP3T.SLDDRW)
 - [cryoelec-bracket-SP3T.SLDPRT](https://github.com/lafefspietz/MEMSduino/raw/refs/heads/main/cryoelec-bracket-SP3T.SLDPRT)
 - [cryoelec-bracket-SP3T.STL](https://github.com/lafefspietz/MEMSduino/raw/refs/heads/main/cryoelec-bracket-SP3T.STL)
 - [cryoelec-bracket-SP3T.pdf](https://github.com/lafefspietz/MEMSduino/raw/refs/heads/main/cryoelec-bracket-SP3T.pdf)
 - [6_port_controller.ino](https://github.com/lafefspietz/MEMSduino/raw/refs/heads/main/6_port_controller.ino)
 - [6button-6eopixel.SchDoc](https://github.com/lafefspietz/MEMSduino/raw/refs/heads/main/6button-6eopixel.SchDoc)
 - [6button-6neopixel-BOM.xlsx](https://github.com/lafefspietz/MEMSduino/raw/refs/heads/main/6button-6neopixel-BOM.xlsx)
 - [6button-6neopixel-gerbers.zip](https://github.com/lafefspietz/MEMSduino/raw/refs/heads/main/6button-6neopixel-gerbers.zip)
 - [6button-6neopixel.PcbDoc](https://github.com/lafefspietz/MEMSduino/raw/refs/heads/main/6button-6neopixel.PcbDoc)
 - [6button-6neopixels.PrjPcb](https://github.com/lafefspietz/MEMSduino/raw/refs/heads/main/6button-6neopixels.PrjPcb)
 - [6button-6neopixels.PrjPcbStructure](https://github.com/lafefspietz/MEMSduino/raw/refs/heads/main/6button-6neopixels.PrjPcbStructure)
 - [9-port-controller.ino](https://github.com/lafefspietz/MEMSduino/raw/refs/heads/main/9-port-controller.ino)
 - [AN-1304-A-box-modifications.SLDDRW](https://github.com/lafefspietz/MEMSduino/raw/refs/heads/main/AN-1304-A-box-modifications.SLDDRW)
 - [AN-1304-A-box-modifications.SLDPRT](https://github.com/lafefspietz/MEMSduino/raw/refs/heads/main/AN-1304-A-box-modifications.SLDPRT)
 - [AN-1304-A-box-modifications.STEP](https://github.com/lafefspietz/MEMSduino/raw/refs/heads/main/AN-1304-A-box-modifications.STEP)
 - [AN-1304-A-box-modifications.pdf](https://github.com/lafefspietz/MEMSduino/raw/refs/heads/main/AN-1304-A-box-modifications.pdf)
 - [AN-1304-A-lid-modifications.SLDDRW](https://github.com/lafefspietz/MEMSduino/raw/refs/heads/main/AN-1304-A-lid-modifications.SLDDRW)
 - [AN-1304-A-lid-modifications.SLDPRT](https://github.com/lafefspietz/MEMSduino/raw/refs/heads/main/AN-1304-A-lid-modifications.SLDPRT)
 - [AN-1304-A-lid-modifications.STEP](https://github.com/lafefspietz/MEMSduino/raw/refs/heads/main/AN-1304-A-lid-modifications.STEP)
 - [AN-1304-A-lid-modifications.pdf](https://github.com/lafefspietz/MEMSduino/raw/refs/heads/main/AN-1304-A-lid-modifications.pdf)
 - [arduino-bracket.SLDDRW](https://github.com/lafefspietz/MEMSduino/raw/refs/heads/main/arduino-bracket.SLDDRW)
 - [arduino-bracket.SLDPRT](https://github.com/lafefspietz/MEMSduino/raw/refs/heads/main/arduino-bracket.SLDPRT)
 - [arduino-bracket.STL](https://github.com/lafefspietz/MEMSduino/raw/refs/heads/main/arduino-bracket.STL)
 - [arduino-bracket.pdf](https://github.com/lafefspietz/MEMSduino/raw/refs/heads/main/arduino-bracket.pdf)
 - [arduino-to-headers-shield-BOM.xlsx](https://github.com/lafefspietz/MEMSduino/raw/refs/heads/main/arduino-to-headers-shield-BOM.xlsx)
 - [arduino-to-headers-shield-gerbers.zip](https://github.com/lafefspietz/MEMSduino/raw/refs/heads/main/arduino-to-headers-shield-gerbers.zip)
 - [arduino-to-headers-shield.PcbDoc](https://github.com/lafefspietz/MEMSduino/raw/refs/heads/main/arduino-to-headers-shield.PcbDoc)
 - [arduino-to-headers-shield.PrjPcb](https://github.com/lafefspietz/MEMSduino/raw/refs/heads/main/arduino-to-headers-shield.PrjPcb)
 - [arduino-to-headers-shield.PrjPcbStructure](https://github.com/lafefspietz/MEMSduino/raw/refs/heads/main/arduino-to-headers-shield.PrjPcbStructure)
 - [arduino-to-headers-shield.SchDoc](https://github.com/lafefspietz/MEMSduino/raw/refs/heads/main/arduino-to-headers-shield.SchDoc)
 - [cryoelec-bracket.SLDDRW](https://github.com/lafefspietz/MEMSduino/raw/refs/heads/main/cryoelec-bracket.SLDDRW)
 - [cryoelec-bracket.SLDPRT](https://github.com/lafefspietz/MEMSduino/raw/refs/heads/main/cryoelec-bracket.SLDPRT)
 - [cryoelec-bracket.STL](https://github.com/lafefspietz/MEMSduino/raw/refs/heads/main/cryoelec-bracket.STL)
 - [cryoelec-bracket.pdf](https://github.com/lafefspietz/MEMSduino/raw/refs/heads/main/cryoelec-bracket.pdf)
 - [front-panel-edge-bracket.SLDDRW](https://github.com/lafefspietz/MEMSduino/raw/refs/heads/main/front-panel-edge-bracket.SLDDRW)
 - [front-panel-edge-bracket.SLDPRT](https://github.com/lafefspietz/MEMSduino/raw/refs/heads/main/front-panel-edge-bracket.SLDPRT)
 - [front-panel-edge-bracket.STL](https://github.com/lafefspietz/MEMSduino/raw/refs/heads/main/front-panel-edge-bracket.STL)
 - [front-panel-edge-bracket.pdf](https://github.com/lafefspietz/MEMSduino/raw/refs/heads/main/front-panel-edge-bracket.pdf)
 - [rack-mount-board-SP6T.SLDDRW](https://github.com/lafefspietz/MEMSduino/raw/refs/heads/main/rack-mount-board-SP6T.SLDDRW)
 - [rack-mount-board-SP6T.SLDPRT](https://github.com/lafefspietz/MEMSduino/raw/refs/heads/main/rack-mount-board-SP6T.SLDPRT)
 - [rack-mount-board-SP6T.pdf](https://github.com/lafefspietz/MEMSduino/raw/refs/heads/main/rack-mount-board-SP6T.pdf)
 - [switch_control_matlab.m](https://github.com/lafefspietz/MEMSduino/raw/refs/heads/main/switch_control_matlab.m)
 - [switch_control_python.py](https://github.com/lafefspietz/MEMSduino/raw/refs/heads/main/switch_control_python.py)

## ARDUINO CODE

```
/*
*  This program uses the Arduino UNO to control a set of 2 SP3T switches in a pair configuration
*  Lafe Spietz, NIST, 2025
*  Version with dual switches and a single supply for the 8 total lines for the 2 switches. Connect the ground by means of the fridge shield.  
*  February 2025 custom for Jake Davidson in the highspeed waveform metrology group at NIST
*/

#include <Adafruit_NeoPixel.h>
#ifdef __AVR__
#endif

// Which pin on the Arduino is connected to the NeoPixels?
// It is very important to change this based on if you have a Mega or UNO, since the A5 pin maps to different digital output pins
// A5 maps to 19 on the UNO and 59 on the Mega  

//#define PIN 59 // MEGA 
#define PIN 19 // UNO

// How many NeoPixels are attached to the Arduino?
#define NUMPIXELS 6 // 
//there are 6

// When setting up the NeoPixel library, we tell it how many pixels,  
// and which pin to use to send signals. Note that for older NeoPixel
// strips you might need to change the third parameter -- see the
// strandtest example for more information on possible values.
Adafruit_NeoPixel pixels(NUMPIXELS, PIN, NEO_GRB + NEO_KHZ800);

//define bit numbers on the Cryoelec controller and map them to Arduino pins

#define switch1_common 2 // DSUB PIN 1
#define switch1_RF1 3    // DSUB PIN 2
#define switch1_RF2 4    // DSUB PIN 3
#define switch1_RF3 5    // DSUB PIN 4
#define switch2_common 6 // DSUB PIN 5
#define switch2_RF1 7    // DSUB PIN 6
#define switch2_RF2 8    // DSUB PIN 7
#define switch2_RF3 9    // DSUB PIN 8

int analog = 0;// variable which reads out the analog input from the button ladder
int delta = 20;//the acceptable difference between an analog value and an expected button state value

int mode = 1;//modes are 1, 2, or 3, which are:
//mode 1: from RF1 on switch 1 to RF3 on switch 2
//mode 2: from RF2 on switch 1 to RF2 on switch 2
//mode 3: from RF3 on switch 1 to RF1 on switch 2

void setup() {
  Serial.begin(9600);//set the baud rate to 9600 baud.

  //Set all bits to digital output mode:
  pinMode(switch1_common,OUTPUT);
  pinMode(switch1_RF1,OUTPUT);
  pinMode(switch1_RF2,OUTPUT);
  pinMode(switch1_RF3,OUTPUT);
  pinMode(switch2_common,OUTPUT);
  pinMode(switch2_RF1,OUTPUT);
  pinMode(switch2_RF2,OUTPUT);
  pinMode(switch2_RF3,OUTPUT);

  //set all pins low to start off with except common pins, which are high
  digitalWrite(switch1_common,HIGH);
  digitalWrite(switch1_RF1,LOW);
  digitalWrite(switch1_RF2,LOW);
  digitalWrite(switch1_RF3,LOW);
  digitalWrite(switch2_common,HIGH);
  digitalWrite(switch2_RF1,LOW);
  digitalWrite(switch2_RF2,LOW);
  digitalWrite(switch2_RF3,LOW);

  pixels.begin(); // INITIALIZE NeoPixel strip object (REQUIRED)
  pixels.setPixelColor(0, pixels.Color(0, 0, 0));    
  pixels.setPixelColor(1, pixels.Color(0, 0, 0));    
  pixels.setPixelColor(2, pixels.Color(0, 0, 0));    
  pixels.setPixelColor(3, pixels.Color(0, 0, 0));    
  pixels.setPixelColor(4, pixels.Color(0, 0, 0));    
  pixels.setPixelColor(5, pixels.Color(0, 0, 0));   
  
}

void loop() {

  pixels.clear(); // Set all pixel colors to 'off'
  analog = analogRead(A4);//read the analog voltage from the button ladder
  // The first NeoPixel in a strand is #0, second is 1, all the way up
  // to the count of pixels minus one.
  
  // compare the analog value to all of the various button state values.  
  // This is a probe to see which node on a many-stage voltage divider
  //  is connected to the analog pin, which tests which button is pressed.
  // We check again after a milisecond to make sure the button state 
  // is stable and is not part of a transient signal.
  // There are two if statements for each value to ensure that the user has 
  // held the button in that state for at least a millisecond, 
  // in order to prevent responding to transient signal values

  if(analog > 1024 - delta){
    delay(1);
    analog = analogRead(A4);
    if(analog > 1023 - delta){
      mode = 1;
    }
  }
  if(analog > 784 - delta && analog < 784 + delta){
    delay(1);
    analog = analogRead(A4);
    if(analog > 784 - delta && analog < 784 + delta){
      mode = 2;
    }
  }
  if(analog > 596 - delta && analog < 596 + delta){
     delay(1);
     analog = analogRead(A4);
    if(analog > 596 - delta && analog < 596 + delta){
      mode = 3;
    }
  }

  if (Serial.available()) {

    //read serial as ascii integer
     int ser = Serial.read();
     if(ser == 48){    //ASCII for 0
      mode = 0;
     }    
     if(ser == 49){    //ASCII for 1
       mode = 1;
     }
     if(ser == 50){    //ASCII for 2
       mode = 2;
     }
     if(ser == 51){    //ASCII for 3
       mode = 3;
     }

  }

  if(mode == 1){
    pixels.setPixelColor(5, pixels.Color(0, 155, 0));//path 1 green
    pixels.setPixelColor(4, pixels.Color(0, 0, 0));    
    pixels.setPixelColor(3, pixels.Color(0, 0, 0));    
    digitalWrite(switch1_RF1,HIGH);
    digitalWrite(switch1_RF2,LOW);
    digitalWrite(switch1_RF3,LOW);    
    digitalWrite(switch2_RF1,LOW);
    digitalWrite(switch2_RF2,LOW);
    digitalWrite(switch2_RF3,HIGH);    

  }
  if(mode == 2){
    pixels.setPixelColor(5, pixels.Color(0, 0, 0));
    pixels.setPixelColor(4, pixels.Color(0, 155, 0));//path 2 green
    pixels.setPixelColor(3, pixels.Color(0, 0, 0));    
    digitalWrite(switch1_RF1,LOW);
    digitalWrite(switch1_RF2,HIGH);
    digitalWrite(switch1_RF3,LOW);    
    digitalWrite(switch2_RF1,LOW);
    digitalWrite(switch2_RF2,HIGH);
    digitalWrite(switch2_RF3,LOW);     
  }
  if(mode == 3){
    pixels.setPixelColor(5, pixels.Color(0, 0, 0));
    pixels.setPixelColor(4, pixels.Color(0, 0, 0));    
    pixels.setPixelColor(3, pixels.Color(0, 155, 0));//path 3 green
    digitalWrite(switch1_RF1,LOW);
    digitalWrite(switch1_RF2,LOW);
    digitalWrite(switch1_RF3,HIGH);    
    digitalWrite(switch2_RF1,HIGH);
    digitalWrite(switch2_RF2,LOW);
    digitalWrite(switch2_RF3,LOW);        
  }
  if(mode == 0){
    
    pixels.setPixelColor(0, pixels.Color(0, 0, 0));    
    pixels.setPixelColor(1, pixels.Color(0, 0, 0));    
    pixels.setPixelColor(2, pixels.Color(0, 0, 0));    
    pixels.setPixelColor(3, pixels.Color(0, 0, 0));    
    pixels.setPixelColor(4, pixels.Color(0, 0, 0));    
    pixels.setPixelColor(5, pixels.Color(0, 0, 0));      
    
    digitalWrite(switch1_RF1,LOW);
    digitalWrite(switch1_RF2,LOW);
    digitalWrite(switch1_RF3,LOW);    
    digitalWrite(switch2_RF1,LOW);
    digitalWrite(switch2_RF2,LOW);
    digitalWrite(switch2_RF3,LOW);    

  }

  pixels.show();   // Send the updated pixel colors to the hardware.
  delay(1); // Pause before next pass through loop

}

```

## PYTHON CODE

```
import serial
ser = serial.Serial('COM12', 9600)  # open serial port, replace with correct COM port, found from IDE
ser.write(bytes(str(1), encoding='utf-8')) # replace the number 1 with port number
```

## MATLAB CODE

```

% Use the instrument control app to see what com ports are  connected and
% try connecting and testing. You can also use the Arduino IDE to find out
% what port the Arduino is on.  Change the baud rate to 115200 to interact
% with the serial.  Just send numbers 1 through 9 down the serial to change
% the state.  

switch_controller = instrfind('Type', 'serial', 'Port', 'COM10', 'Tag', '');

% Create the serial port object if it does not exist
% otherwise use the object that was found.
if isempty(switch_controller)
    switch_controller = serial('COM10');
else
    fclose(switch_controller);
    switch_controller = switch_controller(1);
end

fopen(switch_controller);
switch_controller.BaudRate = 9600;

%% bouncing lights test pattern

while true
    for n = 1:9
       fprintf(switch_controller,int2str(n))
       pause(0.05);
    
    end
    
    for n = 1:9
        
       fprintf(switch_controller,int2str(10-n))
       pause(0.05);
    
    end
end

%%  Step switch and take trace

for n = 1:9 
    smatrix.switch1 = n;    
    fprintf(switchotron1,int2str(smatrix.switch1));
    pause(2);
    % take and save trace here

end
```

## LICENSE

This data/work was created by employees of the National Institute of Standards and Technology (NIST), an agency of the Federal Government. Pursuant to title 17 United States Code Section 105, works of NIST employees are not subject to copyright protection in the United States.  This data/work may be subject to foreign copyright.

The data/work is provided by NIST as a public service and is expressly provided “AS IS.” NIST MAKES NO WARRANTY OF ANY KIND, EXPRESS, IMPLIED OR STATUTORY, INCLUDING, WITHOUT LIMITATION, THE IMPLIED WARRANTY OF MERCHANTABILITY, FITNESS FOR A PARTICULAR PURPOSE, NON-INFRINGEMENT AND DATA ACCURACY. NIST does not warrant or make any representations regarding the use of the data or the results thereof, including but not limited to the correctness, accuracy, reliability or usefulness of the data. NIST SHALL NOT BE LIABLE AND YOU HEREBY RELEASE NIST FROM LIABILITY FOR ANY INDIRECT, CONSEQUENTIAL, SPECIAL, OR INCIDENTAL DAMAGES (INCLUDING DAMAGES FOR LOSS OF BUSINESS PROFITS, BUSINESS INTERRUPTION, LOSS OF BUSINESS INFORMATION, AND THE LIKE), WHETHER ARISING IN TORT, CONTRACT, OR OTHERWISE, ARISING FROM OR RELATING TO THE DATA (OR THE USE OF OR INABILITY TO USE THIS DATA), EVEN IF NIST HAS BEEN ADVISED OF THE POSSIBILITY OF SUCH DAMAGES.

To the extent that NIST may hold copyright in countries other than the United States, you are hereby granted the non-exclusive irrevocable and unconditional right to print, publish, prepare derivative works and distribute the NIST data, in any medium, or authorize others to do so on your behalf, on a royalty-free basis throughout the world.

You may improve, modify, and create derivative works of the data or any portion of the data, and you may copy and distribute such modifications or works. Modified works should carry a notice stating that you changed the data and should note the date and nature of any such change. Please explicitly acknowledge the National Institute of Standards and Technology as the source of the data:  Data citation recommendations are provided at https://www.nist.gov/open/license.

Permission to use this data is contingent upon your acceptance of the terms of this agreement and upon your providing appropriate acknowledgments of NIST’s creation of the data/work.

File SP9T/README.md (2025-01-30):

# [SP9T](https://github.com/lafefspietz/MEMSduino/tree/main/SP9T)




# WOOD BOARD

(https://ocoochhardwoods.com/detail/?i=124wo)







[]()











# 3D Printed Plastic Parts















# Diecast Aluminum Enclosure



# Bill of Materials

# Illustrated and Anotated Bill of Materials

# Metal Box

# DC DC conversion

# Relay

# 3d Printed Parts

# Build Instructions

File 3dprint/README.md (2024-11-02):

## [../](../)

# MEMSDuino 3d Print Files

## [files.html](files.html)

## [webeditor.html](webeditor.html)



Print all files in PLA. Use 4-40 brass thread inserts in HV-DCDC-bracket, arduino-bracket and front-panel-edge-bracket and 0-80 thread inserts in cryoelec-bracket.  Designs compatible with both hot press and press fit thread inserts.  This repository contains designs for five parts, and for each part there is an .STL file for sending to the 3d printer, a SolidWorks part file, a SolidWorks drawing file, a .pdf of the drawing, and an image of the pdf.  The zip file contains all five files for all 5 parts.  Which files you print depend on the use case, and are listed below in the list of STL files in this document.

 - [4-40 press fit brass thread inserts(EZ-LOK  ‎240-004-BR)](https://www.amazon.com/Z-LOK-Threaded-Insert-Plastic/dp/B08QJHXR7P/)
 - [0-80 Brass Thread Inserts(E-Z LOK 240-000-BR)](https://www.amazon.com/Z-LOK-Threaded-Insert-Plastic/dp/B08QJJDCW1/)
 - [3dprint-all-files.zip](3dprint-all-files.zip)

## COTS SP6T Build Bill of Materials

 - [7x 4-40 press fit brass thread inserts(EZ-LOK  ‎240-004-BR)](https://www.amazon.com/Z-LOK-Threaded-Insert-Plastic/dp/B08QJHXR7P/)
 - [4x 0-80 Brass Thread Inserts(E-Z LOK 240-000-BR)](https://www.amazon.com/Z-LOK-Threaded-Insert-Plastic/dp/B08QJJDCW1/)
 - 3/32" drill for pilot holes in wood
 - 7x 4-40 1/4" steel machine screws
 - 4x 0-80 1/4" machine screws
 - 6x #6 Phillips head wood screws
 - [arduino-bracket.STL (print 1)](arduino-bracket.STL)
 - [cryoelec-bracket.STL (print 1)](cryoelec-bracket.STL)
 - [front-panel-edge-bracket.STL (print 2)](front-panel-edge-bracket.STL)

## Custom SPnT build

 - [11x 4-40 press fit brass thread inserts(EZ-LOK  ‎240-004-BR)](https://www.amazon.com/Z-LOK-Threaded-Insert-Plastic/dp/B08QJHXR7P/)
  - 3/32" drill for pilot holes in wood
 - 11x 4-40 1/4" steel machine screws
 - 10x #6 Phillips head wood screws
 - [1x arduino-bracket.STL](arduino-bracket.STL)
 - [1x HV-DCDC-bracket.STL](HV-DCDC-bracket.STL)
 - [2x front-panel-center-bracket.STL](front-panel-center-bracket.STL)
 - [2x front-panel-edge-bracket.STL](front-panel-edge-bracket.STL)

## All STL Files

 - [HV-DCDC-bracket.STL(print 1, custom only) 4 g of filament, 14 minutes print time](HV-DCDC-bracket.STL)
 - [arduino-bracket.STL(print 1, all use cases) 4 g of filament, 17 minutes print time](arduino-bracket.STL)
 - [cryoelec-bracket.STL(print 1, for COTS controller) 4 g of filament, 16 minutes print time](cryoelec-bracket.STL)
 - [front-panel-center-bracket.STL(print 2, SP9T only) 1 g of filament, 7 minutes print time](front-panel-center-bracket.STL)
 - [front-panel-edge-bracket.STL(print 2, all use cases) 3 g of filament, 14 minutes print time](front-panel-edge-bracket.STL)
 - [MEMSduino-3dprint-STL.zip](MEMSduino-3dprint-STL.zip)

## Drawings

 
 
 
 
 

## Photos of Prints






## All Files

 - [HV-DCDC-bracket.SLDDRW](HV-DCDC-bracket.SLDDRW)
 - [HV-DCDC-bracket.SLDPRT](HV-DCDC-bracket.SLDPRT)
 - [HV-DCDC-bracket.STL](HV-DCDC-bracket.STL)
 - [HV-DCDC-bracket.pdf](HV-DCDC-bracket.pdf)
 - [HV-DCDC-bracket.png](HV-DCDC-bracket.png)
 - [arduino-bracket.SLDDRW](arduino-bracket.SLDDRW)
 - [arduino-bracket.SLDPRT](arduino-bracket.SLDPRT)
 - [arduino-bracket.STL](arduino-bracket.STL)
 - [arduino-bracket.pdf](arduino-bracket.pdf)
 - [arduino-bracket.png](arduino-bracket.png)
 - [cryoelec-bracket.SLDDRW](cryoelec-bracket.SLDDRW)
 - [cryoelec-bracket.SLDPRT](cryoelec-bracket.SLDPRT)
 - [cryoelec-bracket.STL](cryoelec-bracket.STL)
 - [cryoelec-bracket.pdf](cryoelec-bracket.pdf)
 - [cryoelec-bracket.png](cryoelec-bracket.png)
 - [front-panel-center-bracket.SLDDRW](front-panel-center-bracket.SLDDRW)
 - [front-panel-center-bracket.SLDPRT](front-panel-center-bracket.SLDPRT)
 - [front-panel-center-bracket.STL](front-panel-center-bracket.STL)
 - [front-panel-center-bracket.pdf](front-panel-center-bracket.pdf)
 - [front-panel-center-bracket.png](front-panel-center-bracket.png)
 - [front-panel-edge-bracket.SLDDRW](front-panel-edge-bracket.SLDDRW)
 - [front-panel-edge-bracket.SLDPRT](front-panel-edge-bracket.SLDPRT)
 - [front-panel-edge-bracket.STL](front-panel-edge-bracket.STL)
 - [front-panel-edge-bracket.pdf](front-panel-edge-bracket.pdf)
 - [front-panel-edge-bracket.png](front-panel-edge-bracket.png)

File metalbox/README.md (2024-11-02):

## [../](../)

# MEMSDuino Metal Box Files

## [files.html](files.html)

## [webeditor.html](webeditor.html)

(https://www.digikey.com/en/products/detail/bud-industries/AN-1304-A/5804538)




This part is the same for both builds. You will need a milling machine and some machine tools or to find a shop who can do the modifications.  In the latter case, you will need to send the machine shop the .pdf drawings and the .STEP files.

## All Files

 - [MEMSduino-metalbox.zip (all files)](MEMSduino-metalbox.zip)
 - [AN-1304-A-box-modifications.SLDDRW](AN-1304-A-box-modifications.SLDDRW)
 - [AN-1304-A-box-modifications.SLDPRT](AN-1304-A-box-modifications.SLDPRT)
 - [AN-1304-A-box-modifications.STEP](AN-1304-A-box-modifications.STEP)
 - [AN-1304-A-box-modifications.pdf](AN-1304-A-box-modifications.pdf)
 - [AN-1304-A-lid-modifications.SLDDRW](AN-1304-A-lid-modifications.SLDDRW)
 - [AN-1304-A-lid-modifications.SLDPRT](AN-1304-A-lid-modifications.SLDPRT)
 - [AN-1304-A-lid-modifications.STEP](AN-1304-A-lid-modifications.STEP)
 - [AN-1304-A-lid-modifications.pdf](AN-1304-A-lid-modifications.pdf)

## Parts and Tools needed

 - AN-1304-A diecast aluminum box from Bud Industries
 - Milling machine 
 - 1/8" end mill
 - 3/8" end mill
 - Center drill
 - Edge finder
 - 3/16" long 4-40 standoffs
 - #43 drill
 - 4-40 tap, tapping tool, cutting oil
 - 0.75" long 4-40 brass socket cap screw
 - Either a DSUB board mount connector(for SP9T) or a DSUB solder cup connector(for COTS SP6T) depending on which build

(https://www.mcmaster.com/91075A462/)

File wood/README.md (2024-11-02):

## [../](../)

# MEMSDuino Wood Files

## [files.html](files.html)

## [webeditor.html](webeditor.html)

 
 
 
 
 

For whichever build you are doing, print out the appropriate .pdf in 1 to 1 scale, cut out the templates, tape them together, and use them to transfer information to the wood and then drill all the holes. A hand drill is sufficient for this build.  Use #6 wood screws to attach 3d printed brackets to the wood and 3/4" long 4-40 brass socket head screws to attach the die-cast aluminum enclosure to the board. Brass Flared-Collar Knurled-Head Thumb Screws 10-32 Thread Size, 3/4" Long, McMaster Carr part number 92421A645 is used to mount the instrument in a 19 inch rack mount, assuming 10-32 threads on the rack.

 - [rack-mount-board-SP6T.pdf](rack-mount-board-SP6T.pdf)
 - [rack-mount-board-SP9T.pdf](rack-mount-board-SP9T.pdf)





## All Files

 - [MEMSduino-wood.zip (all files)](MEMSduino-wood.zip)
 - [rack-mount-board-SP6T.SLDDRW](rack-mount-board-SP6T.SLDDRW)
 - [rack-mount-board-SP6T.SLDPRT](rack-mount-board-SP6T.SLDPRT)
 - [rack-mount-board-SP6T.pdf](rack-mount-board-SP6T.pdf)
 - [rack-mount-board-SP6T.png](rack-mount-board-SP6T.png)
 - [rack-mount-board-SP9T.SLDDRW](rack-mount-board-SP9T.SLDDRW)
 - [rack-mount-board-SP9T.SLDPRT](rack-mount-board-SP9T.SLDPRT)
 - [rack-mount-board-SP9T.pdf](rack-mount-board-SP9T.pdf)
 - [rack-mount-board-SP9T.png](rack-mount-board-SP9T.png)

## Parts and Tools needed
 
 - #6 wood screws
 - Knurled 10-32 screws 
 - 1/8 inch drill bit
 - 3/32 inch drill bit
 - 1/4 inch drill bit
 - 7/32 inch drill bit
 - Wood saw
 - Awl or other sharp metal point
 - Scissors, tape, printer, pen

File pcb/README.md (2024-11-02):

## [../](../)

# MEMSDuino PCB Files

To order circuit boards, upload the .zip of the Gerber files to a PCB manufacturer web page.  These boards look the best with black soldermask and white silkscreen.

## [webeditor.html](webeditor.html)

## [files.html](files.html)

## SP6T Files

 - [6button-6neopixel-gerbers.zip](6button-6neopixel-gerbers.zip)
 - [6button-6eopixel.SchDoc](6button-6eopixel.SchDoc)
 - [6button-6neopixel.PcbDoc](6button-6neopixel.PcbDoc)
 - [6button-6neopixels.PrjPcb](6button-6neopixels.PrjPcb)
 - [6button-6neopixels.PrjPcbStructure](6button-6neopixels.PrjPcbStructure)
 - [arduino-to-headers-shield-gerbers.zip](arduino-to-headers-shield-gerbers.zip)
 - [arduino-to-headers-shield.PcbDoc](arduino-to-headers-shield.PcbDoc)
 - [arduino-to-headers-shield.PrjPcb](arduino-to-headers-shield.PrjPcb)
 - [arduino-to-headers-shield.PrjPcbStructure](arduino-to-headers-shield.PrjPcbStructure)
 - [arduino-to-headers-shield.SchDoc](arduino-to-headers-shield.SchDoc)

## SP9T Files

 - [9button-9neopixel-gerbers.zip](9button-9neopixel-gerbers.zip)
 - [9button-9neopixel.PcbDoc](9button-9neopixel.PcbDoc)
 - [9button-9neopixel.SchDoc](9button-9neopixel.SchDoc)
 - [9button-9neopixels.PrjPcb](9button-9neopixels.PrjPcb)
 - [9button-9neopixels.PrjPcbStructure](9button-9neopixels.PrjPcbStructure)
 - [DB25-relay-HV-control-gerbers.zip](DB25-relay-HV-control-gerbers.zip)
 - [DB25-relay-HV-control.PcbDoc](DB25-relay-HV-control.PcbDoc)
 - [DB25-relay-HV-control.PrjPcb](DB25-relay-HV-control.PrjPcb)
 - [DB25-relay-HV-control.PrjPcbStructure](DB25-relay-HV-control.PrjPcbStructure)
 - [DB25-relay-HV-control.SchDoc](DB25-relay-HV-control.SchDoc)
 - [arduino-to-headers-shield-gerbers.zip](arduino-to-headers-shield-gerbers.zip)
 - [arduino-to-headers-shield.PcbDoc](arduino-to-headers-shield.PcbDoc)
 - [arduino-to-headers-shield.PrjPcb](arduino-to-headers-shield.PrjPcb)
 - [arduino-to-headers-shield.PrjPcbStructure](arduino-to-headers-shield.PrjPcbStructure)
 - [arduino-to-headers-shield.SchDoc](arduino-to-headers-shield.SchDoc)

## All Files

 - [MEMSduino-pcb.zip](MEMSduino-pcb.zip)
 - [6button-6neopixel-gerbers.zip](6button-6neopixel-gerbers.zip)
 - [6button-6eopixel.SchDoc](6button-6eopixel.SchDoc)
 - [6button-6neopixel.PcbDoc](6button-6neopixel.PcbDoc)
 - [6button-6neopixels.PrjPcb](6button-6neopixels.PrjPcb)
 - [6button-6neopixels.PrjPcbStructure](6button-6neopixels.PrjPcbStructure)
 - [9button-9neopixel-gerbers.zip](9button-9neopixel-gerbers.zip)
 - [9button-9neopixel.PcbDoc](9button-9neopixel.PcbDoc)
 - [9button-9neopixel.SchDoc](9button-9neopixel.SchDoc)
 - [9button-9neopixels.PrjPcb](9button-9neopixels.PrjPcb)
 - [9button-9neopixels.PrjPcbStructure](9button-9neopixels.PrjPcbStructure)
 - [DB25-relay-HV-control-gerbers.zip](DB25-relay-HV-control-gerbers.zip)
 - [DB25-relay-HV-control.PcbDoc](DB25-relay-HV-control.PcbDoc)
 - [DB25-relay-HV-control.PrjPcb](DB25-relay-HV-control.PrjPcb)
 - [DB25-relay-HV-control.PrjPcbStructure](DB25-relay-HV-control.PrjPcbStructure)
 - [DB25-relay-HV-control.SchDoc](DB25-relay-HV-control.SchDoc)
 - [arduino-to-headers-shield-gerbers.zip](arduino-to-headers-shield-gerbers.zip)
 - [arduino-to-headers-shield.PcbDoc](arduino-to-headers-shield.PcbDoc)
 - [arduino-to-headers-shield.PrjPcb](arduino-to-headers-shield.PrjPcb)
 - [arduino-to-headers-shield.PrjPcbStructure](arduino-to-headers-shield.PrjPcbStructure)
 - [arduino-to-headers-shield.SchDoc](arduino-to-headers-shield.SchDoc)
 - [PcbLibLafe.PcbLib](PcbLibLafe.PcbLib)
 - [SchlibLafe.SchLib](SchlibLafe.SchLib)

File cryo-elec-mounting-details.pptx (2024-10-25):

## Working on design for cryo-elec mount and redesign of other 3d print parts

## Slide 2


Holes: 0-80 free fit clearance = 1.75 mm = 0.069”
Dimensions of hole rectangle: 29 mm x 73.69 mm (1.142” x 2.901”)
Outer dimensions: 76.36 mm x 31.72 mm

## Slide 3


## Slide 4


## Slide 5


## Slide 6

1

2

3

4

5

6


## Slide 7


https://www.amazon.com/Z-LOK-Threaded-Insert-Plastic/dp/B08QJJDCW1/

https://www.ezlok.com/ezpress-insert-240-000-BR

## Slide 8


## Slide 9


https://www.amazon.com/Phillips-Machine-Screws-Stainless-Thread/dp/B07D6L9M9G/

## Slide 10


Hole depth: 0.188” = 4.7752 mm
Hole width: 0.156” = 3.9624 mm

https://www.ezlok.com/ezpress-insert-240-004-BR

E-Z Lok ‎240-004-BR

https://www.amazon.com/Z-LOK-Threaded-Insert-Plastic/dp/B08QJHXR7P/

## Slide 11


https://www.amazon.com/Stainless-Available-Machine-Screws-Phillips/dp/B07B3XQ5Y2/

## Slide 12


#6 clearance hole: .1495” free fit, round to .150”

https://www.amazon.com/Stainless-Phillips-Screws-Multipurpose-TPOHH/dp/B0CHRWGT8N/

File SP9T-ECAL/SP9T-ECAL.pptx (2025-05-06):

## SP9T-ECAL

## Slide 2


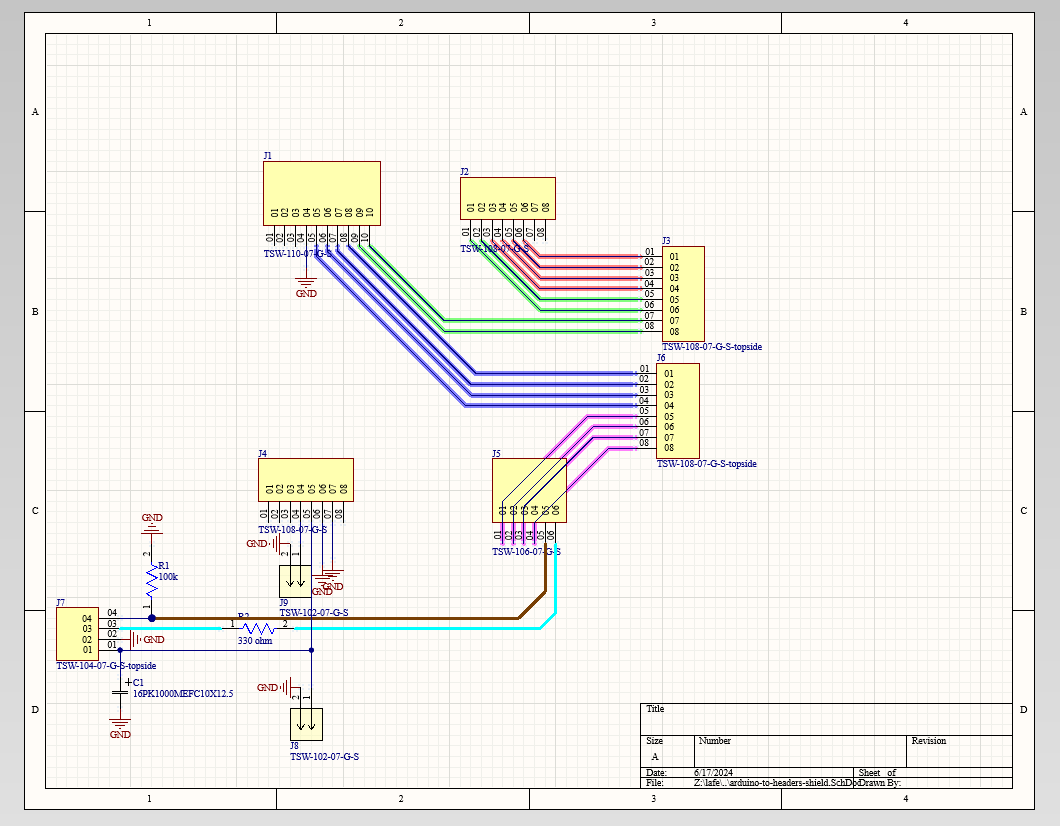
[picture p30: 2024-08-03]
images/arduino-to-headers-shield-altium-schematic-screenshot.png

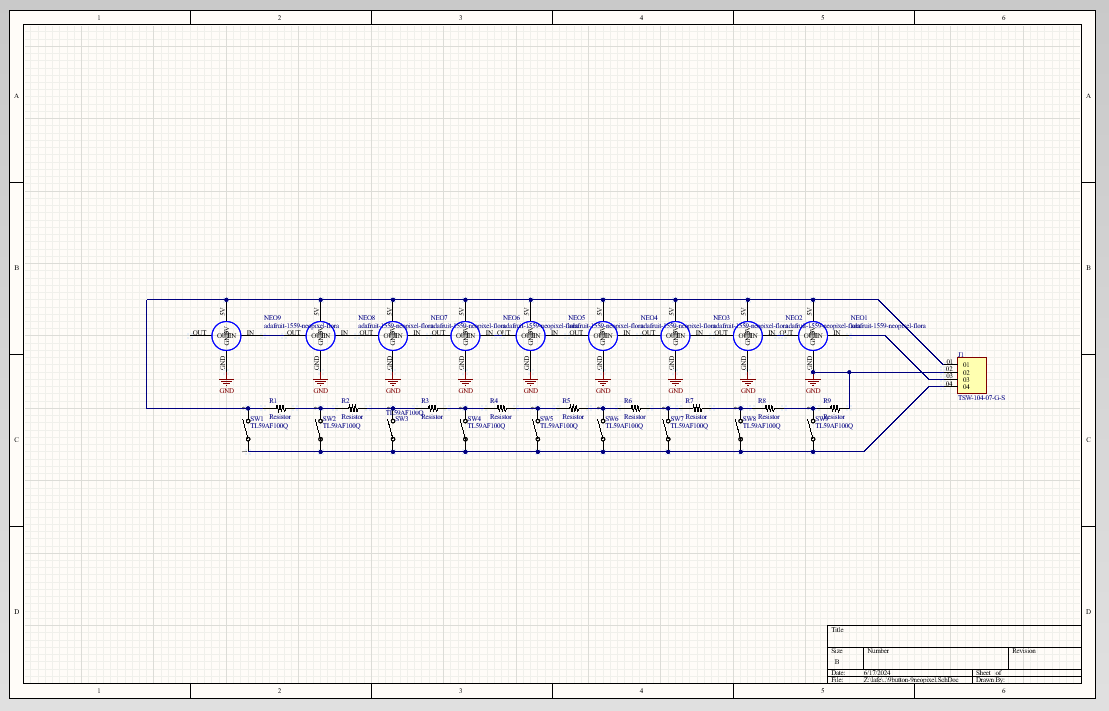
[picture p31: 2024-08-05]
images/9button-9neopixels-schematic-screenshot.png

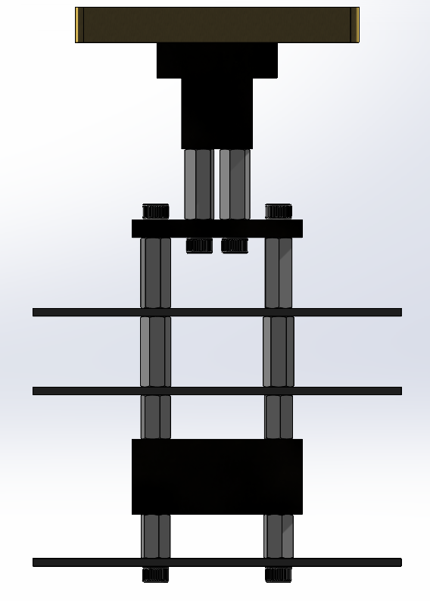
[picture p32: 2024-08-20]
images/Main-Images/Cryogenic-Mounting-Hardware-Main-Image.png

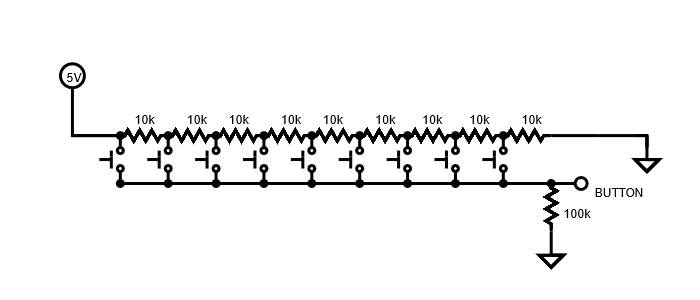
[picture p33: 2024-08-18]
images/buttons-schematic.png

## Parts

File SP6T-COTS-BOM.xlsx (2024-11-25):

description | link to buy | unit price | number | extended price | vendor | vendor part number | manfacturer | manufacturer part number
1/2" White oak board, 4" x 24" | https://ocoochhardwoods.com/detail/?i=124wo | $5.40 | 1 | $5.40 | Ocooch Hardwoods |  | Ocooch Hardwoods
Brass Flared-Collar Knurled-Head Thumb Screws 10-32 Thread Size, 3/4" Long | https://www.mcmaster.com/92421A645/ | $1.62 | 4 | $6.48 | McMaster Carr | 92421A645
#6 wood screws | https://www.amazon.com/Stainless-Phillips-Screws-Multipurpose-TPOHH/dp/B0CHRWGT8N | $0.07 | 8 | $0.56 | Amazon
cryoelec-bracket | https://github.com/lafefspietz/MEMSduino/raw/refs/heads/main/cryoelec-bracket.STL |  | 1 |  | in house prototype
arduino-bracket | https://github.com/lafefspietz/MEMSduino/raw/refs/heads/main/arduino-bracket.STL |  | 1 |  | in house prototype
front-panel-edge-bracket | https://github.com/lafefspietz/MEMSduino/raw/refs/heads/main/front-panel-edge-bracket.STL |  | 2 |  | in house prototype
Brass threaded inserts #4-40 | https://www.3djake.com/ruthex/threaded-insert-4-40-unc-100-pieces | $0.08 | 7 | $0.57 | 3dJake | RUT-GE-4-40x57-001 | ruthex | GE-4-40x57-001
0-80 Brass Thread Inserts(E-Z LOK 240-000-BR) | https://www.amazon.com/Z-LOK-Threaded-Insert-Plastic/dp/B08QJJDCW1/ | $0.47 | 4 | $1.88 | Amazon | B08QJJDCW1 | E-Z LOK | 240-000-BR
0-80 screws 3/16" phillips, stainless | https://www.amazon.com/Machine-Screws-Phillips-Stainless-Steel/dp/B07X8NTTB9/ | $0.14 | 4 | $0.56 | Amazon | B07X8NTTB9 | ‎ Jet Fitting & Supply Corp
Zinc-Plated Steel Pan Head Phillips Screw 4-40 Thread, 1/4" Long | https://www.mcmaster.com/90272A106/ | $0.02 | 9 | $0.16 | McMaster Carr | 90272A106
Diecast aluminum enclosure, AN-1304-A from BUD Industries | https://www.digikey.com/en/products/detail/bud-industries/AN-1304-A/5804538 | $14.90 | 1 | $14.90 | Digikey | 377-2395-ND | Bud Industries | AN-1304-A
Male-Female Threaded Hex Standoff 18-8 Stainless Steel, 3/16" Hex, 7/32" Long, 4-40 to 4-40 Thread | https://www.mcmaster.com/91075A462/ | $3.73 | 2 | $7.46 | McMaster Carr | 91075A462
Brass Socket Head Screw 4-40 Thread Size, 3/4" Long | https://www.mcmaster.com/93465A113/ | $1.20 | 2 | $2.40 | McMaster Carr | 93465A113
Brass Washer for Number 4 Screw Size, 0.12" ID, 0.281" OD | https://www.mcmaster.com/92916A320/ | $0.05 | 2 | $0.10 | McMaster Carr | 92916A320
6button-6neopixel, 152.4 mm x 88.9 mm (6"x3.5") | https://github.com/lafefspietz/MEMSduino/raw/refs/heads/main/6button-6neopixel-gerbers.zip | $5.98 | 1 | $5.98 | PCBWay
arduino-to-headers-shield 53.34 mm x 70.78 mm (2.1" x 2.79") | https://github.com/lafefspietz/MEMSduino/raw/refs/heads/main/arduino-to-headers-shield-gerbers.zip | $1.82 | 1 | $1.82 | PCBWay
100k axial resistor | https://www.digikey.com/en/products/detail/stackpole-electronics-inc/RNF14FTD100K/1706591 | $0.10 | 1 | $0.10 | Digikey | RNF14FTD100KCT-ND | Stackpole Electronics Inc | RNF14FTD100K
10k axial resistor | https://www.digikey.com/en/products/detail/yageo/MFR-25FBF52-10K/13219 | $0.05 | 9 | $0.45 | Digikey | 10.0KXBK-ND | YAGEO | MFR-25FBF52-10K
330 ohm axial resistor | https://www.digikey.com/en/products/detail/stackpole-electronics-inc/CF18JT330R/1741683 | $0.10 | 2 | $0.20 | Digikey | CF18JT330RCT-ND | Stackpole Electronics Inc | CF18JT330R
1000 uF electrolytic capacitor | https://www.digikey.com/en/products/detail/rubycon/16PK1000MEFC10X12-5/3563556 | $0.51 | 1 | $0.51 | Digikey | 1189-1719-ND | Rubycon | 16PK1000MEFC10X12.5
Momentary buttons | https://www.digikey.com/en/products/detail/e-switch/TL59NF160Q/390533 | $0.29 | 6 | $1.74 | Digikey | EG2532TB-ND | E Switch | TL59NF160Q
JUMPER WIRE M/M 6" 20PCS | https://www.digikey.com/en/products/detail/sparkfun-electronics/PRT-12795/5993860 | $2.10 | 1 | $2.10 | Digikey | 1568-1512-ND | Sparkfun | PRT-12795
DB25 panel mount solder cup | https://www.digikey.com/en/products/detail/norcomp-inc/171-025-103L001/858135 | $2.16 | 1 | $2.16 | Digikey | 225ME-ND | NorComp Inc. | 171-025-103L001
Arduino UNO | https://www.digikey.com/en/products/detail/dfrobot/DFR0216/6579366 | $16.90 | 1 | $16.90 | Digikey | 1738-1228-ND | DFRobot | DFR0216
USB A to USB B cable | https://www.digikey.com/en/products/detail/assmann-wsw-components/AK672-2-2/947492 | $1.64 | 1 | $1.64 | Digikey | AE1493-ND | Assmann WSW Components | AK672/2-2
Neopixel programmable RGB LED | https://www.adafruit.com/product/1559 | $1.25 | 6 | $7.50 | Adafruit | 1559 | Adafruit | 1559
2 wire header cable | https://www.amazon.com/ZYAMY-Dupont-Connector-Multicolor-Breadboard/dp/B0B8Z23NWX/ | $0.60 | 1 | $0.60 | Amazon
4 wire header cable | https://www.amazon.com/ZYAMY-Dupont-Connector-Multicolor-Breadboard/dp/B0789F523N/ | $0.79 | 9 | $7.11 | Amazon
8 wire header cable | https://www.amazon.com/ZYAMY-Dupont-Connector-Multicolor-Breadboard/dp/B0789F2Y1T/ | $0.99 | 2 | $1.98 | Amazon
0.1" headers | https://www.amazon.com/Header-Lystaii-Pin-Connector-Electronic/dp/B06ZZN8L9S/ | $0.09 | 3 | $0.27 | Amazon
DB25 to Fischer Cable | https://aivon.fi |  | 1 |  | Aivon
 |  |  |  | $61.02

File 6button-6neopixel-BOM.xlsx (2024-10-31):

description | link to buy | unit price | number | extended price | vendor | vendor part number | manfacturer | manufacturer part number
10k axial resistor | https://www.digikey.com/en/products/detail/yageo/MFR-25FBF52-10K/13219 | $0.02 | 6 | $0.13 | Digikey | 10.0KXBK-ND | Yageo | MFR-25FBF52-10K
SWITCH TACTILE SPST-NO 0.05A 12V | https://www.digikey.com/en/products/detail/e-switch/TL59NF160Q/390533 | $0.27 | 6 | $1.62 | Digikey | EG2532CT-ND | E-Switch | A-DF 25 PP/Z
Flora RGB Smart NeoPixel version 3 - Sheet of 20 | https://www.adafruit.com/product/1559 | $1.25 | 6 | $7.50 | Adafruit | 1559 | Adafruit | 1559
0.1" headers 40 pin strips | https://www.amazon.com/Header-Lystaii-Pin-Connector-Electronic/dp/B06ZZN8L9S/ | $0.09 | 1 | $0.09 | Amazon | B06ZZN8L9S | Lystaii
ZYAMY 10PCS 4P Dupont Line 4P Pins 2.54mm Pitch Female to Female Dupont Cable Connector Multicolor Jumper Wire for Breadboard 20CM | https://www.amazon.com/ZYAMY-Dupont-Connector-Multicolor-Breadboard/dp/B0789F523N/ | $0.79 | 1 | $0.79 | Amazon | B0789F523N | ZYAMY | 8541684769
9button-9neopixel, 228.6 mm x 88.9 mm (9"x3.5") |  | $5.98 | 1 | $5.98 | PCBWay
 |  |  |  | $16.11
 |  |  |  |  |  | $1559.00

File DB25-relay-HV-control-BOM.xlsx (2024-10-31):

description | link to buy | unit price | number | extended price | vendor | vendor part number | manfacturer | manufacturer part number
1 Mohm 1206 SMT resistor 1% | https://www.digikey.com/en/products/detail/yageo/RC1206FR-071ML/728388 | $0.04 | 20 | $0.80 | Digikey | 311-1.00MFRCT-ND | Yageo | RC1206FR-071ML
DB25 board mount connector | https://www.digikey.com/en/products/detail/assmann-wsw-components/A-DF-25-PP-Z/1241794 | $1.17 | 1 | $1.17 | Digikey | AE10940-ND | Assmann | A-DF 25 PP/Z
RELAY REED SIP SPST .5A 5V W/DIO | https://www.digikey.com/en/products/detail/comus-international/3570-1331-053/7497099 | $1.41 | 20 | $28.20 | Digikey | 1835-1117-ND | Comus International | 3570-1331-053
0.1" headers 40 pin strips | https://www.amazon.com/Header-Lystaii-Pin-Connector-Electronic/dp/B06ZZN8L9S/ | $0.09 | 1 | $0.09 | Amazon | B06ZZN8L9S | Lystaii
DB25-relay-HV-control 78.74 mm x 71.12 mm (3.1"x2.8") |  | $1.82 | 1 | $1.82 | PCBWay
 |  |  |  |  |  | $0.00

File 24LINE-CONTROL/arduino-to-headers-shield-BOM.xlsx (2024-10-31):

description | link to buy | unit price | number | extended price | vendor | vendor part number | manfacturer | manufacturer part number
100k axial resistor | https://www.digikey.com/en/products/detail/stackpole-electronics-inc/RNF14FTD100K/1706591 | $0.10 | 1 | $0.10 | Digikey | RNF14FTD100KCT-ND | Stackpole Electronics | RNF14FTD100K
330 ohm axial resistor | https://www.digikey.com/en/products/detail/stackpole-electronics-inc/CF18JT330R/1741683 | $0.10 | 1 | $0.10 | Digikey | CF18JT330RCT-ND | Stackpole Electronics | CF18JT330R
1000 uF electrolytic capacitor | https://www.digikey.com/en/products/detail/rubycon/16PK1000MEFC10X12-5/3563556 | $0.51 | 1 | $0.51 | Digikey | 1189-1719-ND | Rubycon | 16PK1000MEFC10X12.5
0.1" headers 40 pin strips | https://www.amazon.com/Header-Lystaii-Pin-Connector-Electronic/dp/B06ZZN8L9S/ | $0.09 | 3 | $0.27 | Amazon | B06ZZN8L9S | Lystaii
arduino-to-headers-shield 53.34 mm x 70.78 mm (2.1" x 2.79") |  | $1.82 | 1 | $1.82 | PCBWay
 |  |  |  |  |  | $0.00

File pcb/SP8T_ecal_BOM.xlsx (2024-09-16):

Comment | manufacturer | Mfgr. Part no. | Description | Designator | Footprint | LibRef | Quantity
DNP | - | - | Connector Header Through Hole 34 position 0.079 _2.00mm_ | J1 | SULLINS_SBH21-NBPN-D17-ST-B | SBH21-NBPN-D17-ST-BK | 1
DNP | - | - |  | J2 | TP_0035 | HEADER 1 | 1
DNP | - | - |  | MH1, MH2, MH3, MH4 | MH | M HOLE1_0 | 4
DNP | - | - |  | MH5, MH6, MH7, MH8, MH9, MH10, MH11 | MH_55 | M HOLE1_0 | 7
TE connectivity CPF0201B56K2E1 | TE Connectivity | CPF0201B75KE1 | CPF 0201 56K2 0.1% 25PPM 1K RL | R1, R2, R3, R4, R5, R6, R7, R8, R9, R10, R11 | FP-ERJ1GN-IPC_C | TE connectivity CPF0201B56K2E1 | 11
TNPW020150R0BEED | TE Connectivity | CPF0201B49R9E1 | RES SMD 50 OHM 0.1% 1/20W 0201 | R12 | FP-ERJ1GN-IPC_C | CMP-1010-00416-3 | 1
PE44490 | Pasternack | PE44490 | SMP, Mini Connector Plug, Male Pin 50 Ohms Board Edge, Cutout; Surface Mount Solder | RF_5, RF_6, RF_7, RF_8, RF_9, RF_10, RF_11, RF_12, RFC1 | CONN-PE44490 | CONN-PE44490 | 9
MM5130 | Menlo Microwave | MM5130 | High power SP4T MEMs switch | U1, U2, U3 | MM5130-NORM_PCB_NOFLOOD | IC-MM5130 | 3
MM5130 | Menlo Microwave | MM5130 | High power SP4T MEMs switch | U8, U9, U10, U11, U12, U13, U14, U15 | MM5130-SP_M_PCB_NOFLOOD | IC-MM5130 | 8

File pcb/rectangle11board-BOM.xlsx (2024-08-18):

Description | Designator | Footprint | Quantity | Mfgr | Mfgr Part No.
DNP | [NoValue], 0 | DNP | 3
DNP | Designator4 | DNP | 1
SMOOTH BORE SMP Connector Plug, Male Pin 50Ohm Surface Mount Solder | J1, J2, J3, J4, J5, J6, J7, J8, J9, J10 | rosenberger-19S201-40ML5 | 10 | Rosenberger | 19S201-40ML5
DNP | J11, J12, J13, J14 | DNP | 4
CPF 0201 56K2 0.1% 25PPM 1K RL | R1, R2, R3, R4, R5, R6, R7, R8, R9, R10, R11, R12 | 0201-resistor | 12 | TE connectivity | CPF0201B56K2E1
High power SP4T MEMs switch | U1, U2, U3, U4 | MM5130-NORM_PCB_NOFLOOD | 4 | Menlo Microwave | MM5130-03NDB-TR

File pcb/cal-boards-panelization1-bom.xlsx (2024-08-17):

Description | Designator | Footprint | Quantity | Mfgr | Mfgr Part No.
Fiducial | 1, 2, 3, 4, 5,6 | fiducial | 6
50 Ohm resistor | R1, R2, R3, R4, R5, R6 | 0201-resistor | 6 | TE connectivity | CPF0201B49R9E1
SMP-straight-19S141-40ML5 | J1,J2 | rosenberger-19S201-40ML5 | 78 | Rosenberger | 19S141-40ML5
SMP-straight-19S10H-40ML5 | J3 | rosenberger-19S201-40ML5 | 16 | Rosenberger | 19S10H-40ML5

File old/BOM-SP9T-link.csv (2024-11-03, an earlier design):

link
https://ocoochhardwoods.com/detail/?i=124wo
https://www.mcmaster.com/92421A645/
https://www.amazon.com/Stainless-Phillips-Screws-Multipurpose-TPOHH/dp/B0CHRWGT8N
https://github.com/lafefspietz/MEMSduino/raw/refs/heads/main/HV-DCDC-bracket.STL
https://github.com/lafefspietz/MEMSduino/raw/refs/heads/main/arduino-bracket.STL
https://github.com/lafefspietz/MEMSduino/raw/refs/heads/main/front-panel-edge-bracket.STL
https://github.com/lafefspietz/MEMSduino/raw/refs/heads/main/front-panel-center-bracket.STL
https://www.3djake.com/ruthex/threaded-insert-4-40-unc-100-pieces
https://www.mcmaster.com/90272A106/
https://www.digikey.com/en/products/detail/bud-industries/AN-1304-A/5804538
https://www.mcmaster.com/91075A462/
https://www.mcmaster.com/93465A113/
https://www.mcmaster.com/92916A320/
https://www.amazon.com/KUNCAN-Converter-Cable-Voltage-Connector/dp/B01ID90K4A/?th=1
https://www.amazon.com/Voltage-Converter-Vintage-Indicator-80V-380V/dp/B09D93QNYK
https://www.digikey.com/en/products/detail/3m/SFTW203-1-16-BL-SPL/22044171
https://github.com/lafefspietz/MEMSduino/raw/refs/heads/main/9button-9neopixel-gerbers.zip
https://github.com/lafefspietz/MEMSduino/raw/refs/heads/main/arduino-to-headers-shield-gerbers.zip
https://github.com/lafefspietz/MEMSduino/raw/refs/heads/main/DB25-relay-HV-control-gerbers.zip
https://www.digikey.com/en/products/detail/stackpole-electronics-inc/RNF14FTD100K/1706591
https://www.digikey.com/en/products/detail/yageo/MFR-25FBF52-10K/13219
https://www.digikey.com/en/products/detail/stackpole-electronics-inc/CF18JT330R/1741683
https://www.digikey.com/en/products/detail/rubycon/16PK1000MEFC10X12-5/3563556
https://www.digikey.com/en/products/detail/e-switch/TL59NF160Q/390533
https://www.digikey.com/en/products/detail/yageo/RC1206FR-071ML/728388
https://www.digikey.com/en/products/detail/assmann-wsw-components/A-DF-25-PP-Z/1241794
https://www.digikey.com/en/products/detail/comus-international/3570-1331-053/7497099
https://www.digikey.com/en/products/detail/dfrobot/DFR0216/6579366
https://www.digikey.com/en/products/detail/assmann-wsw-components/AK672-2-2/947492
https://www.adafruit.com/product/1559
https://www.amazon.com/ZYAMY-Dupont-Connector-Multicolor-Breadboard/dp/B0B8Z23NWX/
https://www.amazon.com/ZYAMY-Dupont-Connector-Multicolor-Breadboard/dp/B0789F523N/
https://www.amazon.com/ZYAMY-Dupont-Connector-Multicolor-Breadboard/dp/B0789F2Y1T/
https://www.amazon.com/Header-Lystaii-Pin-Connector-Electronic/dp/B06ZZN8L9S/

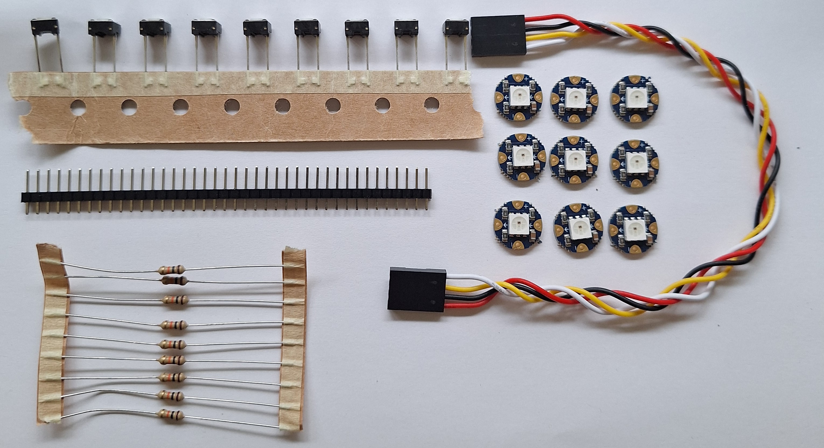
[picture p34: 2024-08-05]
images/control-board-parts-photo.jpg

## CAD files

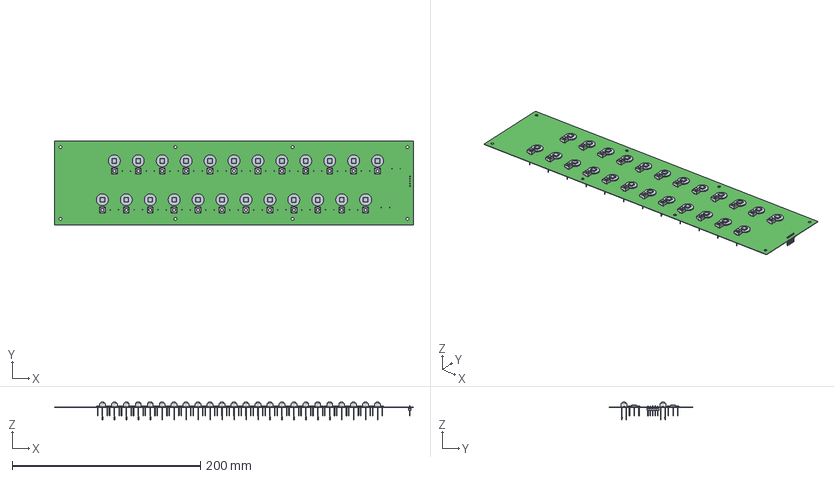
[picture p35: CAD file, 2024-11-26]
24LINE-CONTROL/24line-control-panel.step
381.0 x 88.9 x 18.6 mm
TL59AF100Q x 24
half-inch-round-neopixel-board x 24
TSW-105-07-G-S_body
T-1S6-07-TSW-1-07-5-S

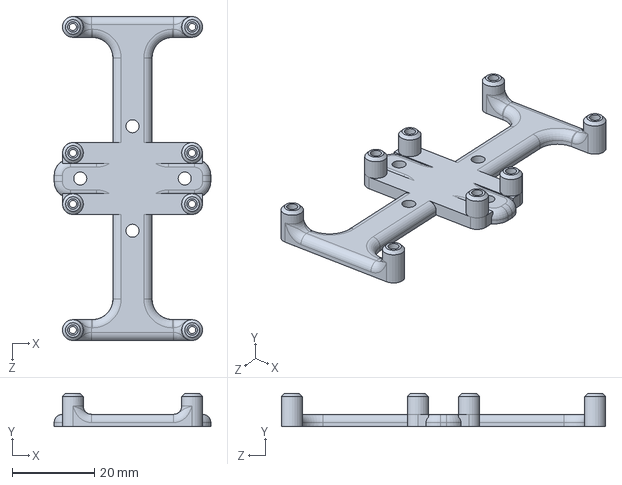
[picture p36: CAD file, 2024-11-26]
DUAL-SP3T-COTS/cryoelec-bracket-SP3T.SLDPRT
38.1 x 8.08 x 78.8 mm

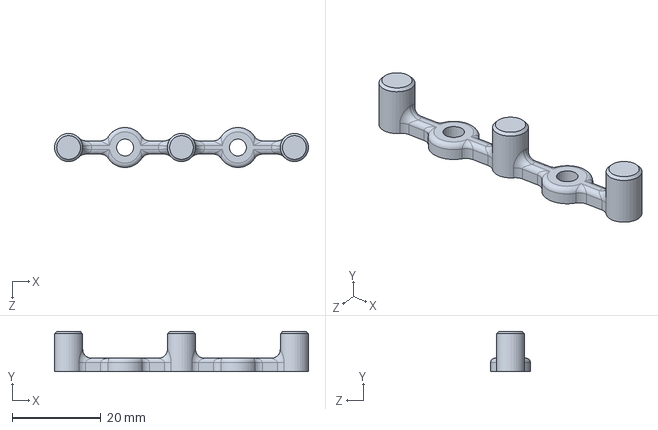
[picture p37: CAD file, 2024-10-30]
front-panel-center-bracket.SLDPRT
57.1 x 9.00 x 9.00 mm

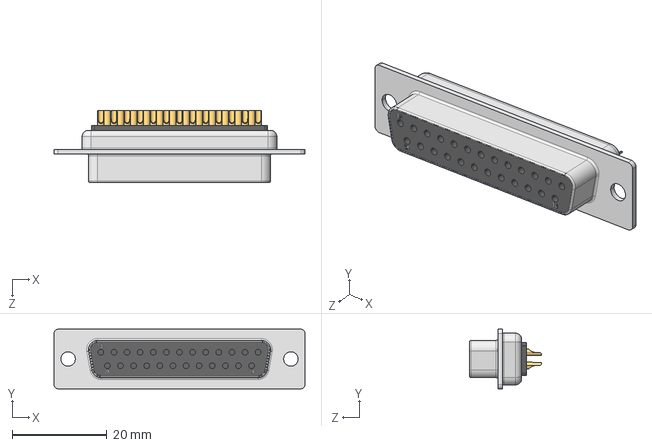
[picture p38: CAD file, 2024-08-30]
machining/171-025-203.STEP
53.0 x 12.6 x 15.3 mm

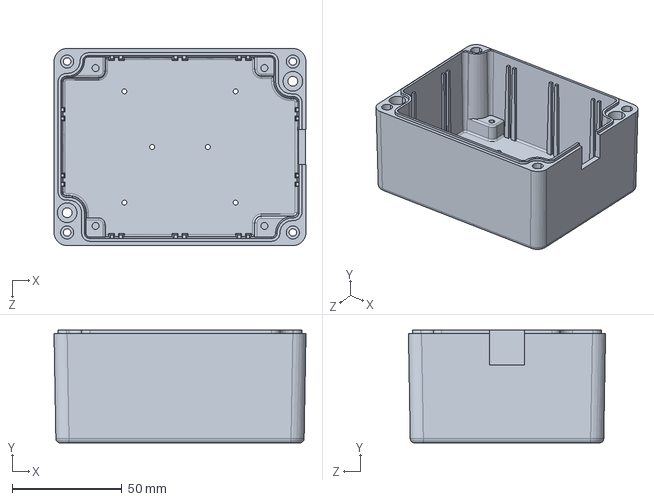
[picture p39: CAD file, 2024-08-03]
metal-box/images/AN-1304-A-box-modifications.SLDPRT
115.0 x 51.5 x 90.0 mm

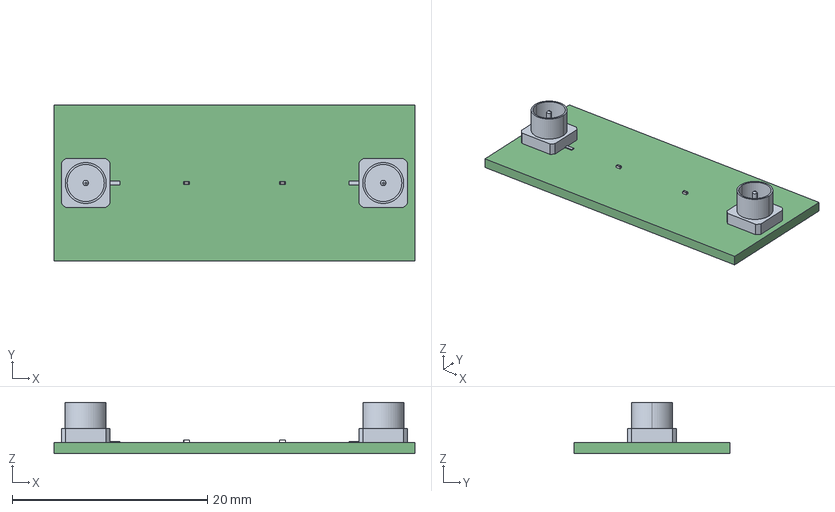
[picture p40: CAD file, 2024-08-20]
pcb/calboards/load-cal-board-1point2in.step
37.0 x 16.0 x 5.26 mm
Panasonic Logo x 2
19S141-40ML5-mymodel x 2

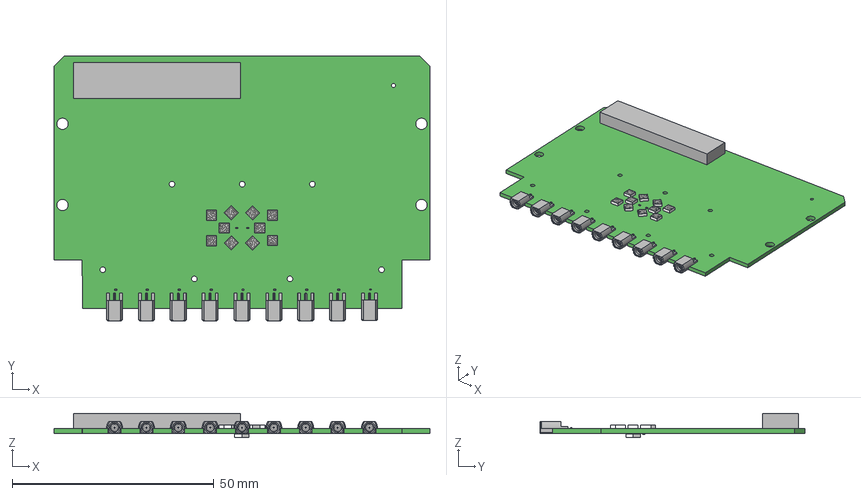
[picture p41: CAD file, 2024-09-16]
pcb/NC_Menlo Micro SP8T RF Board_04212024.step
93.2 x 65.6 x 6.01 mm
Panasonic Logo x 12
Extruded
MM5130_model x 11
PE44490_3D_RGB8421504 x 9

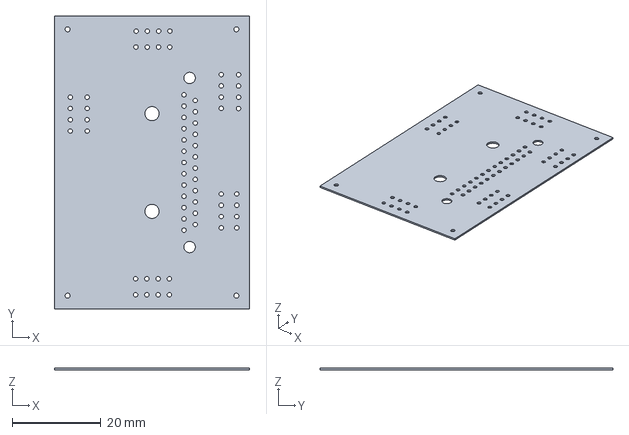
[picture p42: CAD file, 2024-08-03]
SP9T/microd-header-adapter-board-rev2.step
44.0 x 66.0 x 0.411 mm

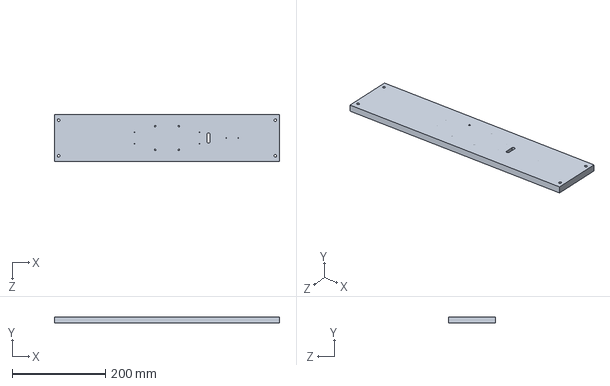
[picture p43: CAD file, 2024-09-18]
DUAL-SP3T-COTS/rack-mount-board-SP6T.SLDPRT
482.6 x 12.7 x 101.6 mm

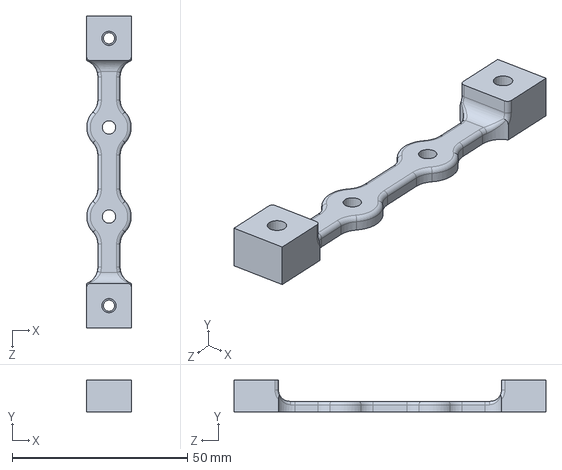
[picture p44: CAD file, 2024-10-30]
front-panel-edge-bracket.SLDPRT
12.7 x 9.00 x 88.9 mm

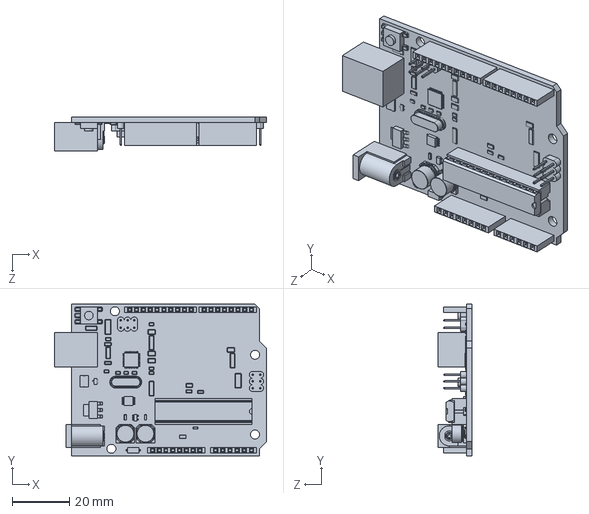
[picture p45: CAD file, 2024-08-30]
machining/Arduino_Uno_Rev3_colored.SLDPRT
74.0 x 53.0 x 12.0 mm

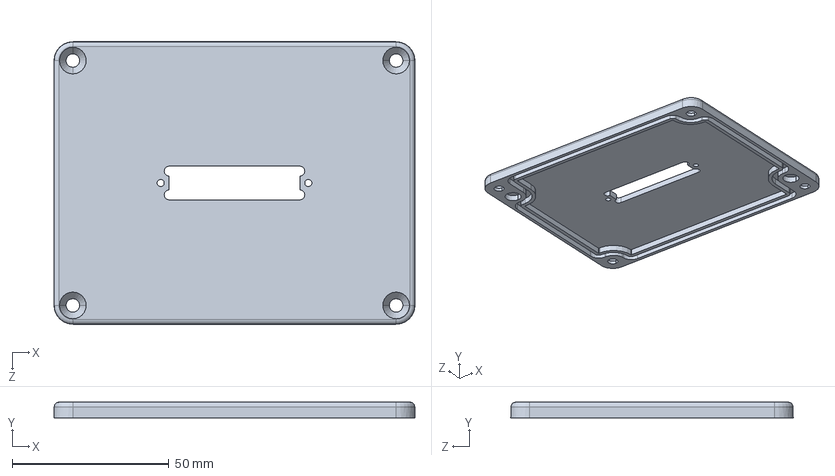
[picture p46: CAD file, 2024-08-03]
metal-box/images/AN-1304-A-lid-modifications.SLDPRT
115.0 x 5.00 x 90.0 mm

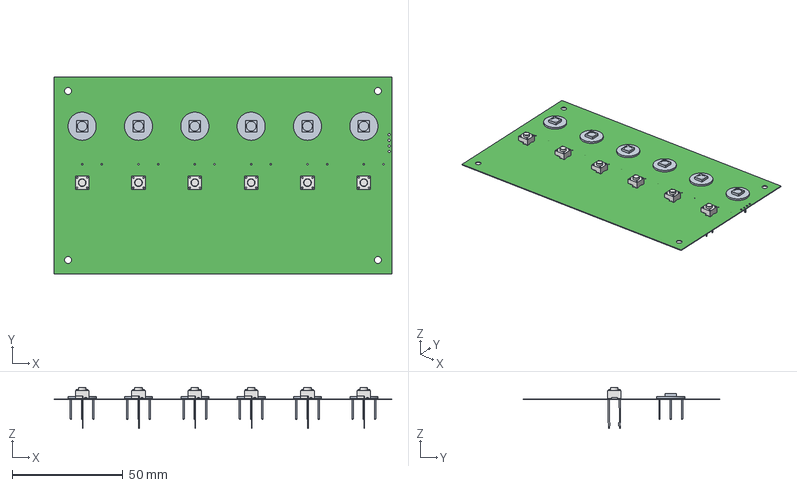
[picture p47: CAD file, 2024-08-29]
pcb/6button-6neopixel.step
152.4 x 88.9 x 18.6 mm
TL59AF100Q x 6
half-inch-round-neopixel-board x 6

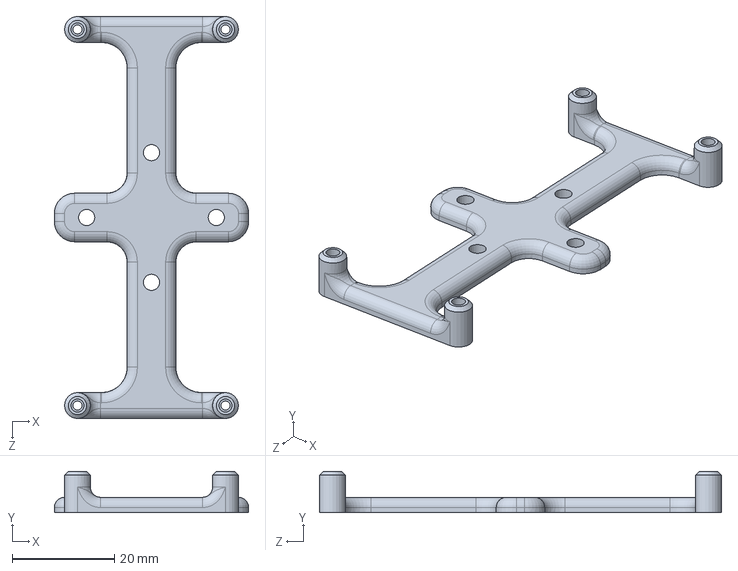
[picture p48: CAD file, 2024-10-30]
cryoelec-bracket.SLDPRT
38.1 x 8.08 x 78.8 mm

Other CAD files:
machining/cold-assembly.SLDASM
pcb/calboards/thru-cal-board-1point2in.step
pcb/calboards/10cm-chip-cal-board-1point2in.step
pcb/rectangle11board.step
AN-1304-A-box-modifications.SLDDRW
AN-1304-A-box-modifications.STEP
AN-1304-A-lid-modifications.SLDDRW
AN-1304-A-lid-modifications.STEP
DUAL-SP3T-COTS/cryoelec-bracket-SP3T.SLDDRW
DUAL-SP3T-COTS/cryoelec-bracket-SP3T.STL
DUAL-SP3T-COTS/rack-mount-board-SP6T.SLDDRW
HV-DCDC-bracket.SLDDRW
HV-DCDC-bracket.SLDPRT
HV-DCDC-bracket.STL
arduino-bracket-noscrews.SLDPRT
arduino-bracket-noscrews.STL
arduino-bracket.SLDDRW
arduino-bracket.SLDPRT
arduino-bracket.STL
cryoelec-bracket.SLDDRW
cryoelec-bracket.STL
front-panel-center-bracket.SLDDRW
front-panel-center-bracket.STL
front-panel-edge-bracket.SLDDRW
front-panel-edge-bracket.STL
machining/171-025-203.SLDPRT
machining/90272A106_Zinc-Plated Steel Pan Head Phillips Screw.SLDPRT
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

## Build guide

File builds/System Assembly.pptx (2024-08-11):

## System Assembly

## System elements

- Bud Box
- Wood board
- Arduino Shield circuit board
- 90 V DC DC power supply
- Arduino UNO programming
- DB25 relay board
- Front panel control boards(SP9T, SP8T +eCal, SP6T)
- 3d printed parts
- Cold MicroD breakout board
- Cold mechanical assembly

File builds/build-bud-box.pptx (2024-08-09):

## Bud Box

MEMSDuino
Lafe Spietz
NIST
Summer 2024

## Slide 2

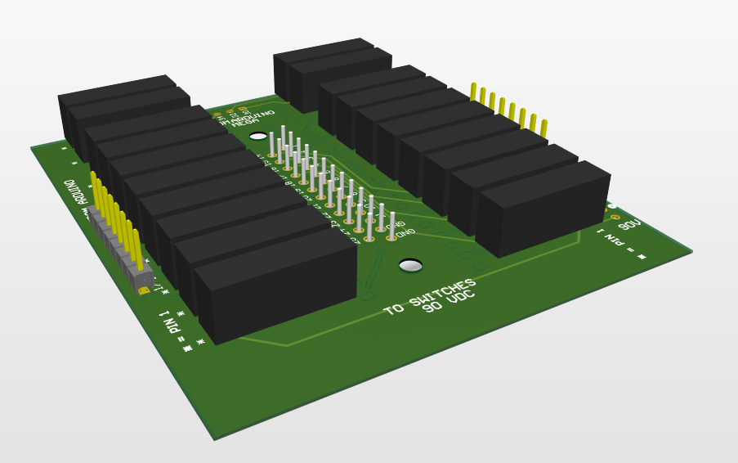
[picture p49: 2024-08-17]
images/db25-relay-assembly-render-rotate2.png

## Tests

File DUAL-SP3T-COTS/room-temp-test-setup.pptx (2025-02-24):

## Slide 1

Room temperature test setup, Feb 24, 2025

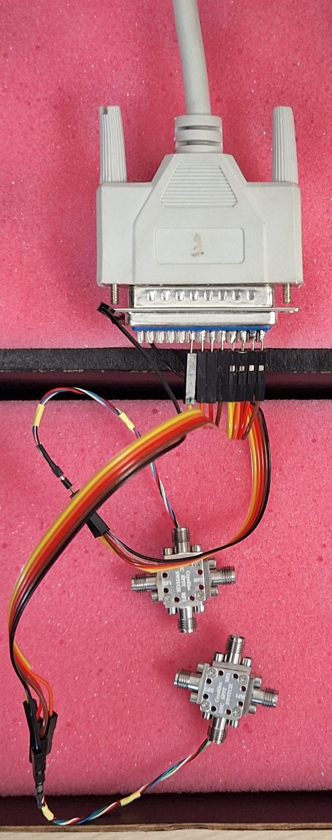
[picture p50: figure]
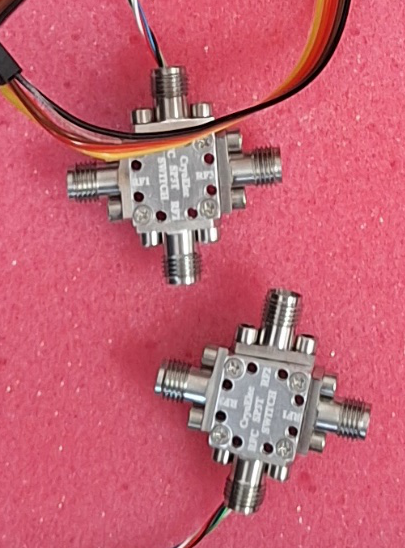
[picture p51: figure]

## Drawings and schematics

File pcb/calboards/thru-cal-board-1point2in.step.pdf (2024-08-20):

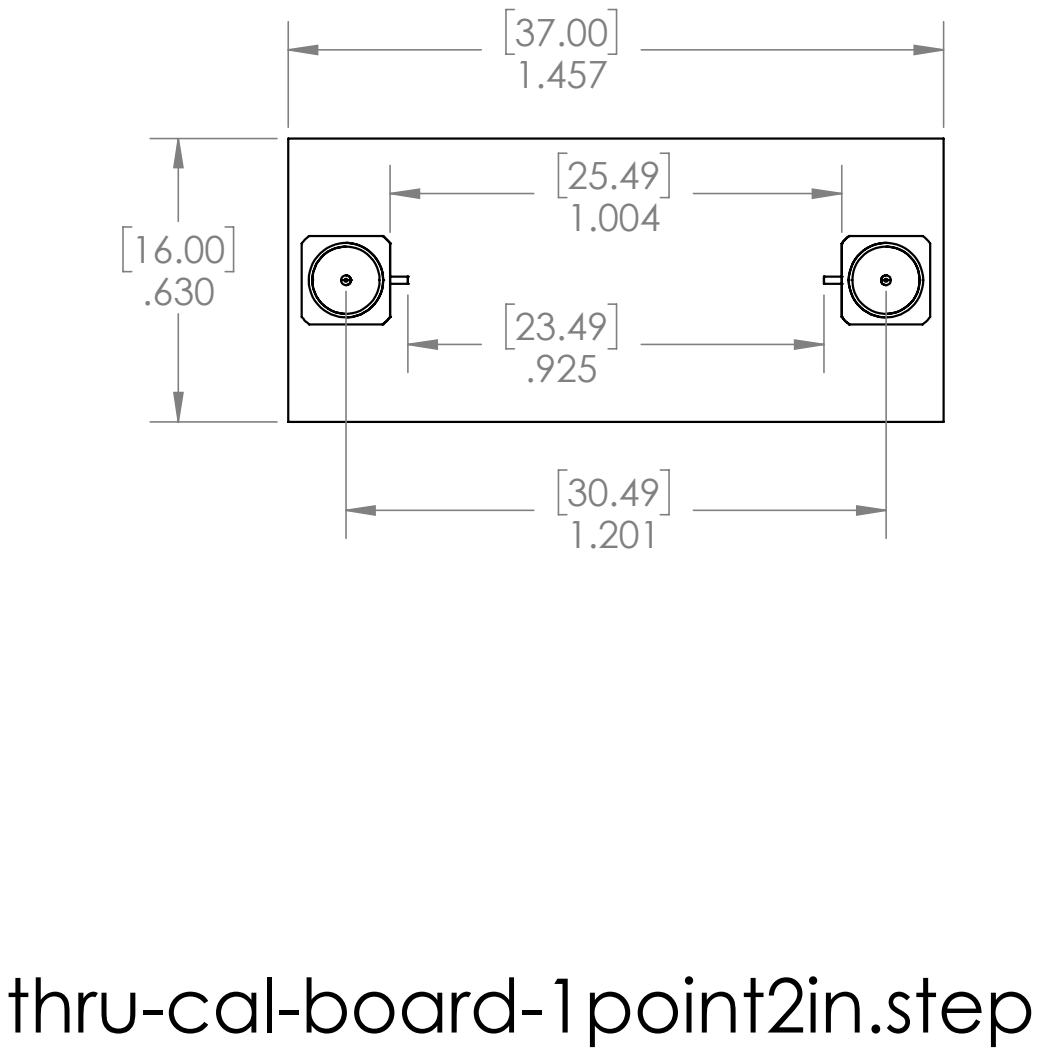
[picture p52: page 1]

thru-cal-board-1point2in.step

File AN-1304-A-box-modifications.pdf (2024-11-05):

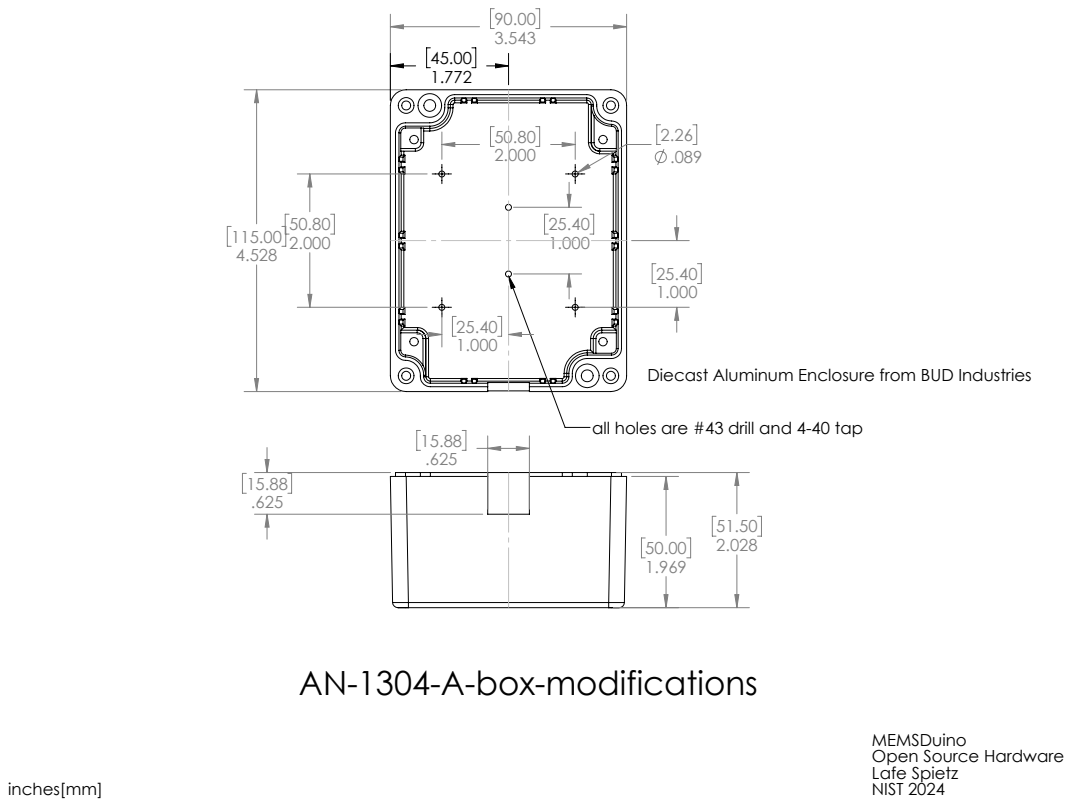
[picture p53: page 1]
inches[mm]; NIST 2024

Diecast Aluminum Enclosure from BUD Industries

all holes are #43 drill and 4-40 tap

AN-1304-A-box-modifications

MEMSDuino
Open Source Hardware
Lafe Spietz

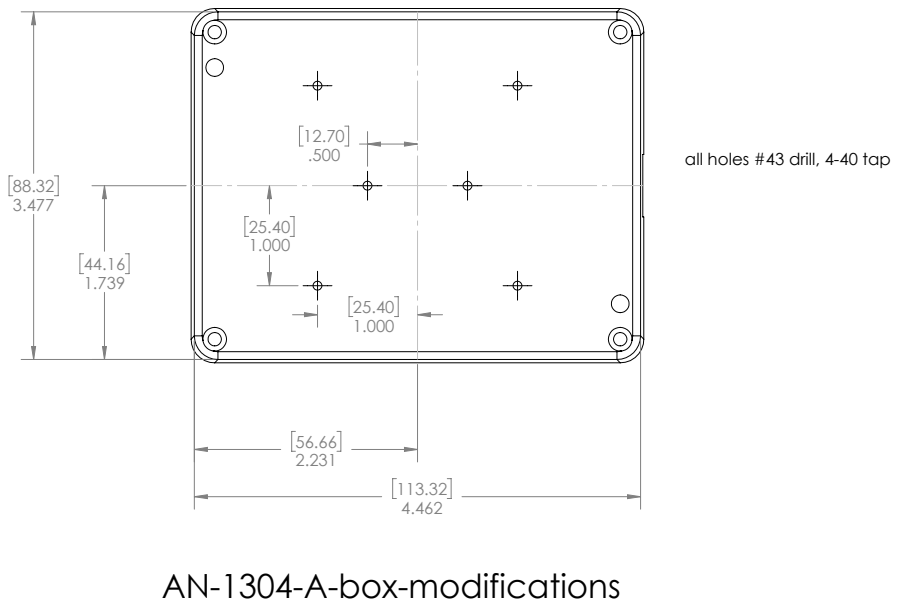
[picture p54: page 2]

all holes #43 drill, 4-40 tap

AN-1304-A-box-modifications

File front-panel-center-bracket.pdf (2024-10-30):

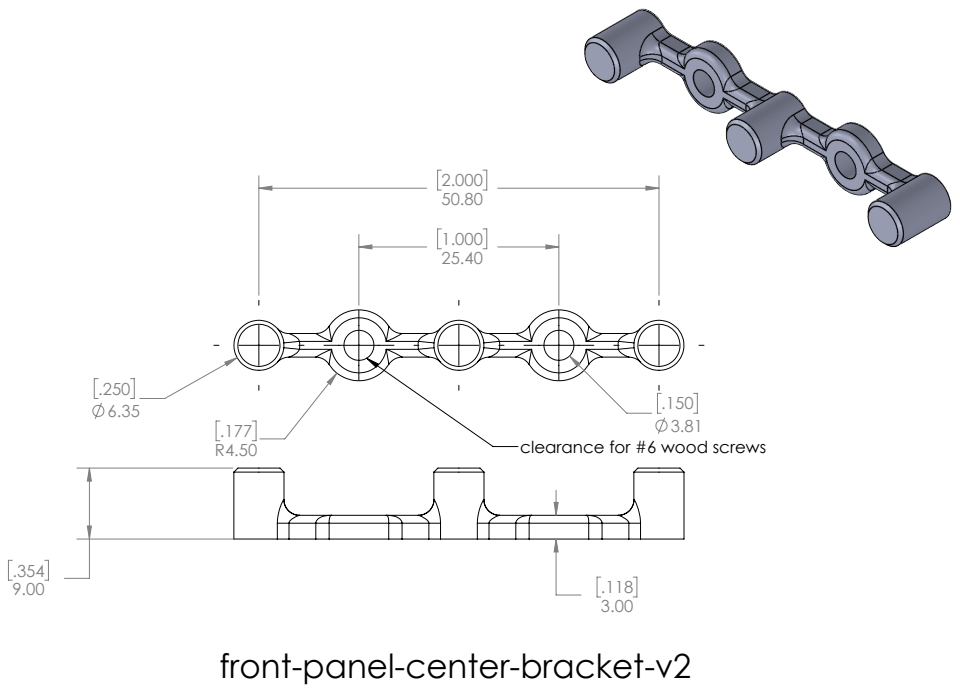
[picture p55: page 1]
clearance for #6 wood screws

front-panel-center-bracket-v2

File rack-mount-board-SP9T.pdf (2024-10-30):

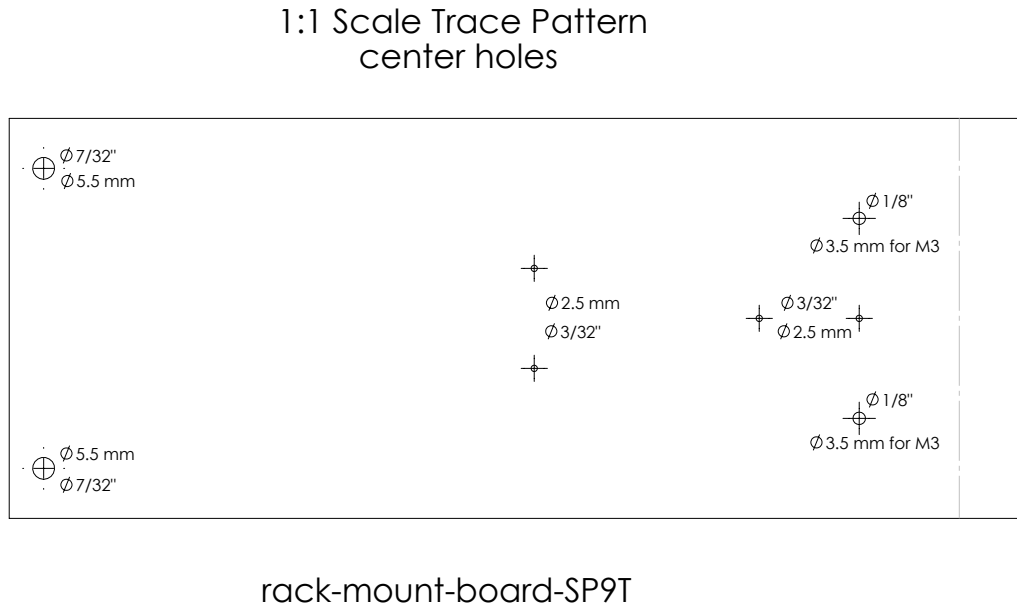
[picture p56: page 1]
3.5 mm for M3

1:1 Scale Trace Pattern
center holes

rack-mount-board-SP9T

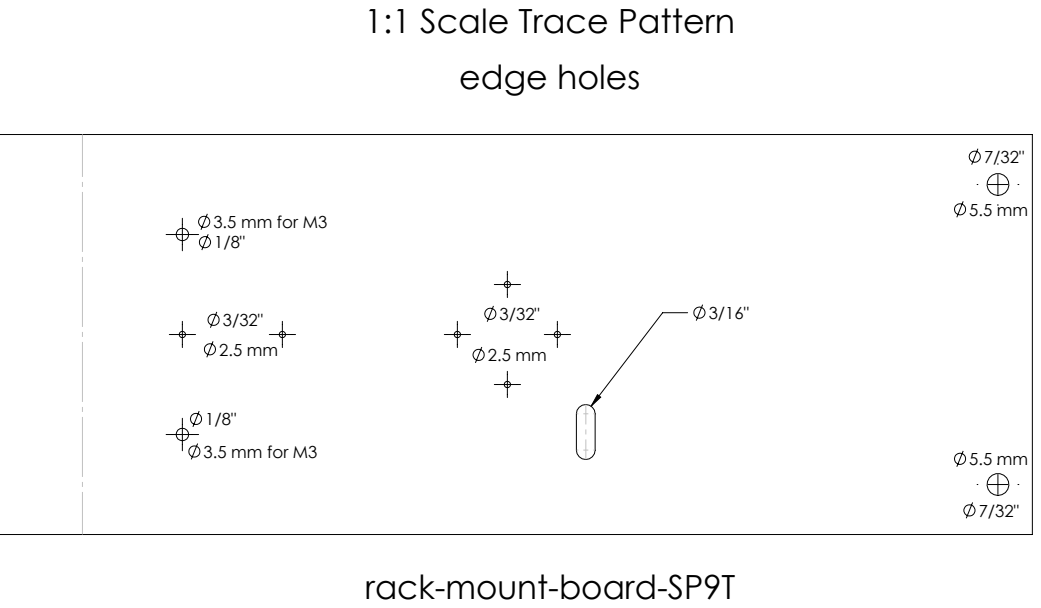
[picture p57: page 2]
3.5 mm for M3

1:1 Scale Trace Pattern
edge holes

rack-mount-board-SP9T

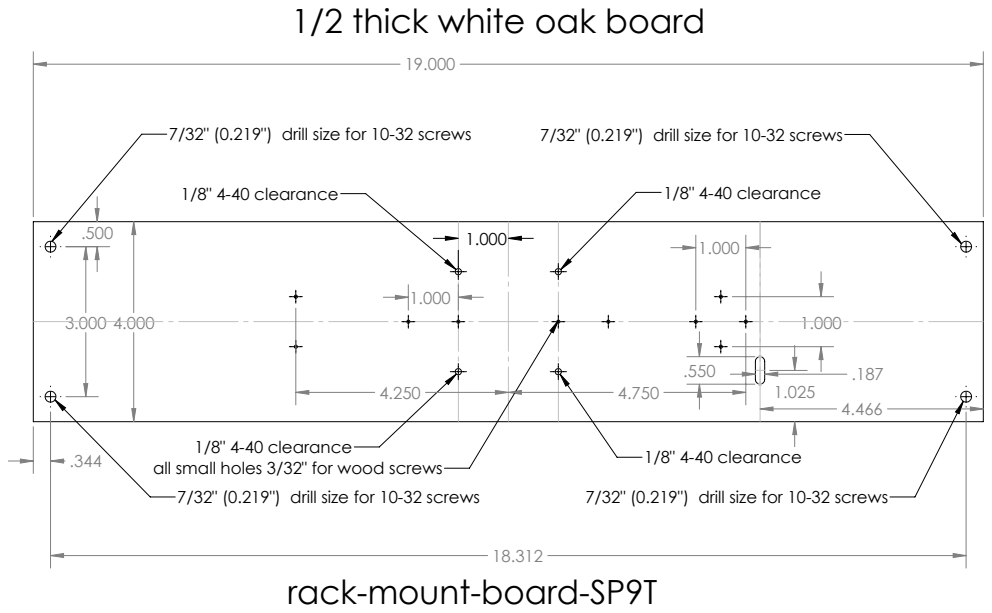
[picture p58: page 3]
1/8" 4-40 clearance; 1/8" 4-40 clearance all small holes 3/32" for wood screws

1/2 thick white oak board

7/32" (0.219") drill size for 10-32 screws

rack-mount-board-SP9T

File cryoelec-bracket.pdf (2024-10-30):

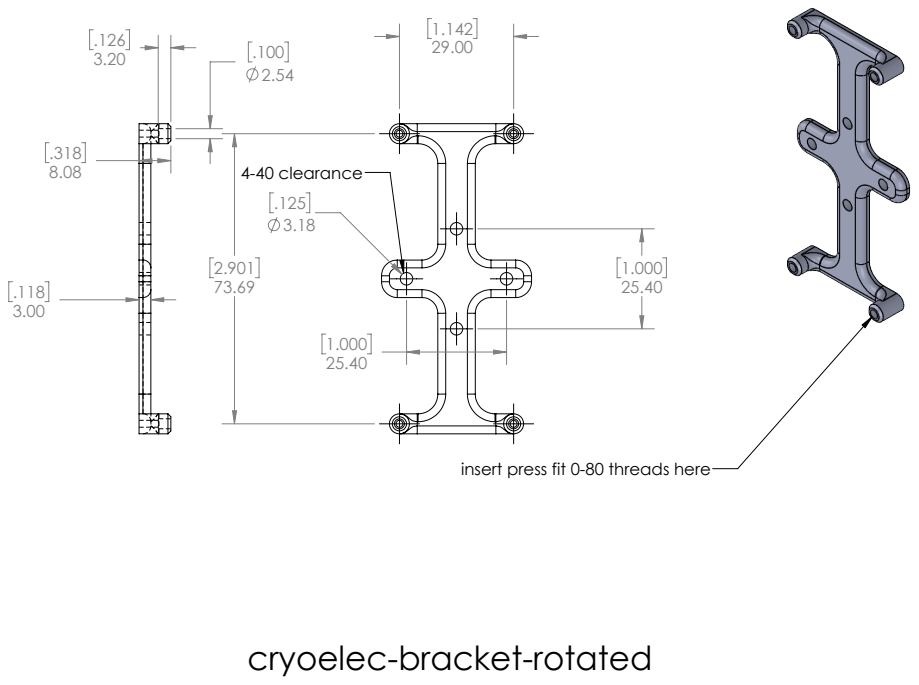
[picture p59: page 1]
4-40 clearance

insert press fit 0-80 threads here

cryoelec-bracket-rotated

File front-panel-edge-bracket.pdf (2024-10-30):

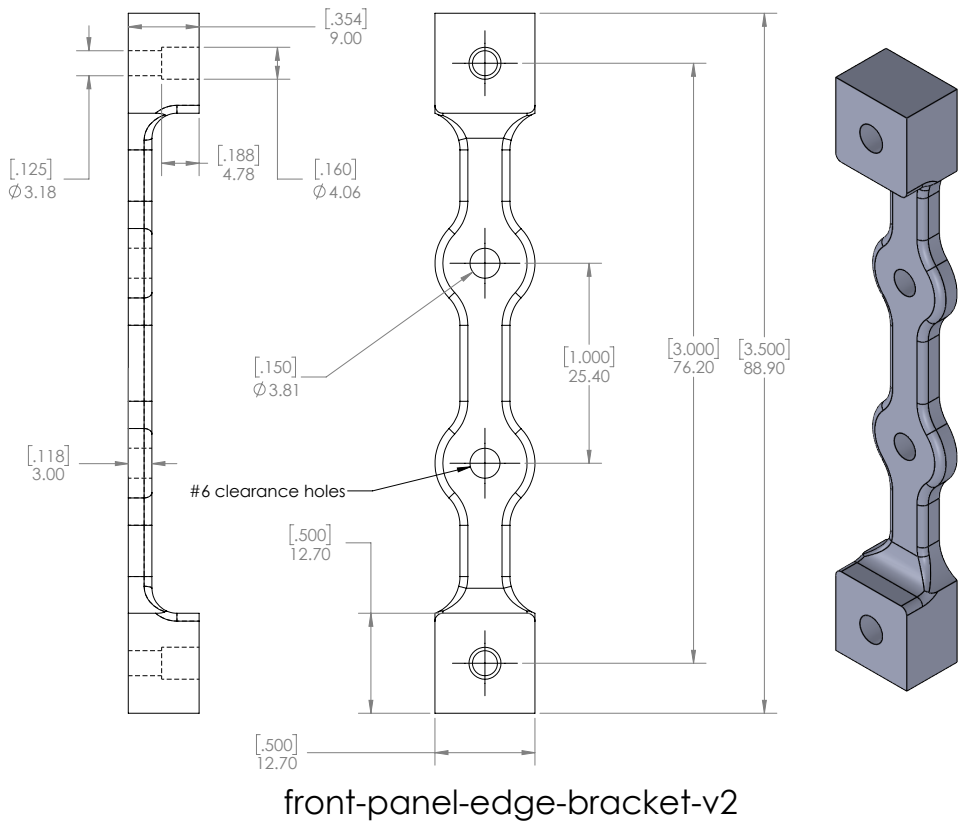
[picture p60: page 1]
#6 clearance holes

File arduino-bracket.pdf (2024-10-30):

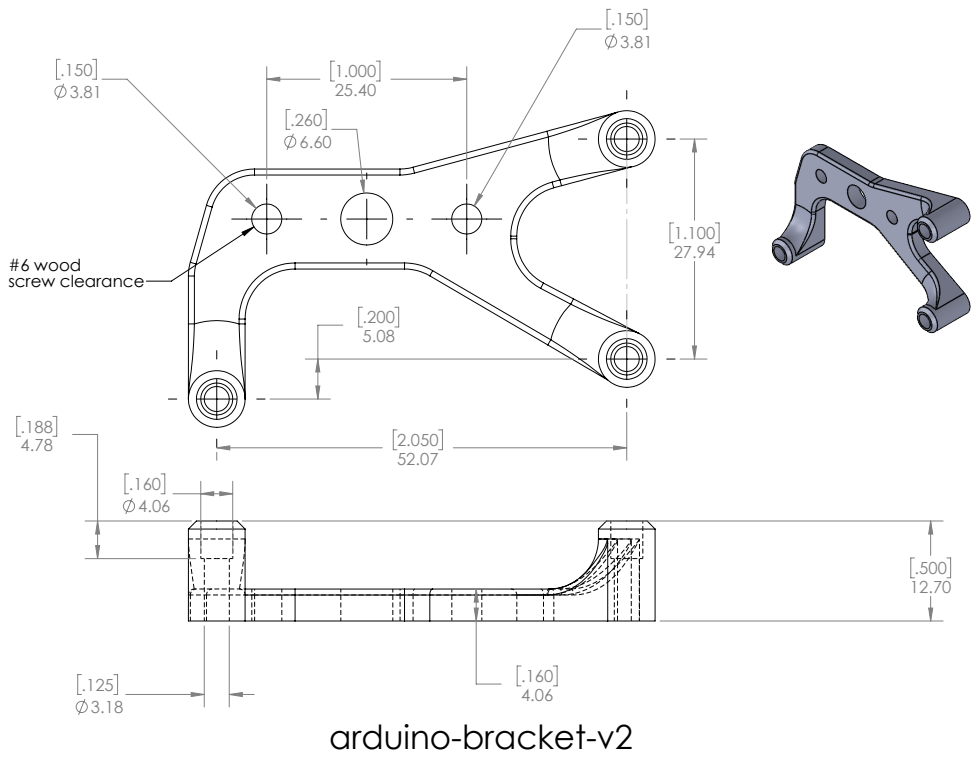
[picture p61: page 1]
#6 wood screw clearance

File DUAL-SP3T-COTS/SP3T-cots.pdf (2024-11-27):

# MEMSDUINO: SP3T COTS

2

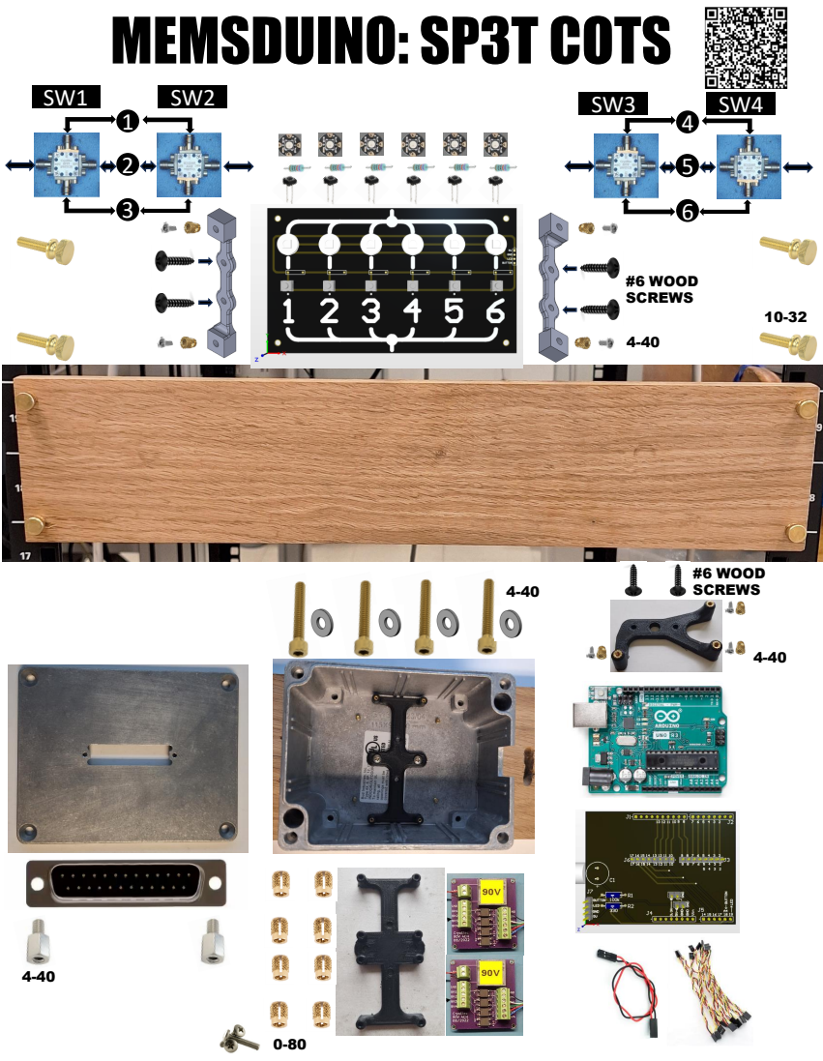
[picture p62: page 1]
#6 WOOD SCREWS

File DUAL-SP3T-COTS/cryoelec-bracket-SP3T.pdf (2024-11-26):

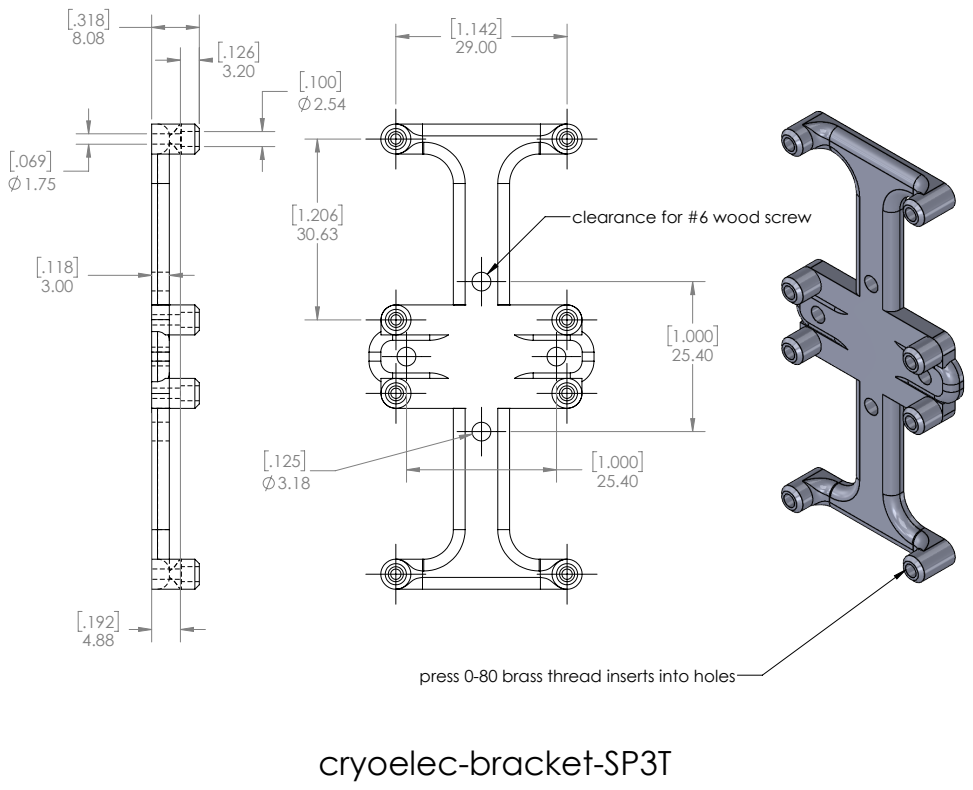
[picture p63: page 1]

clearance for #6 wood screw

press 0-80 brass thread inserts into holes
cryoelec-bracket-SP3T

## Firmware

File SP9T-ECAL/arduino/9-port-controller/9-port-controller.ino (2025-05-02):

#include <Adafruit_NeoPixel.h>
#ifdef __AVR__
#endif

// Which pin on the Arduino is connected to the NeoPixels?
#define PIN 19 // A5 on UNO is pin 19

// How many NeoPixels are attached to the Arduino?
#define NUMPIXELS 9 // 
//there are 9

// When setting up the NeoPixel library, we tell it how many pixels,  
// and which pin to use to send signals. Note that for older NeoPixel
// strips you might need to change the third parameter -- see the
// strandtest example for more information on possible values.
Adafruit_NeoPixel pixels(NUMPIXELS, PIN, NEO_GRB + NEO_KHZ800);


#define NOT_SP8T_1 54 //UNO pin 14, A0
#define NOT_SP8T_2 55 //UNO pin 15, A1
#define NOT_SP8T_7 56 //UNO pin 16, A2
#define NOT_SP8T_8 57 //UNO pin 17, A3

#define U4_123 2
#define U4_456 3
#define U4_789 4
#define U4_COM 5

#define U1_1 54 //UNO pin 14, A0
#define U1_2 55 //UNO pin 15, A1
#define U1_3 56 //UNO pin 16, A2
#define U1_COM 57 //UNO pin 17, A3

#define U2_4 10
#define U2_5 11
#define U2_6 12
#define U2_COM 13

#define U3_7 6
#define U3_8 7
#define U3_9 8
#define U3_COM 9


int analog = 0;
int delta = 20;
int mode = 1;//modes are 1,2,3,4,5,6,7,8,9 which are pixel 8,7,6,5,4,3,2,1, and 0 respectively
int cycle = 0;//variable for cycling colors as test pattern with switch off

void setup() {
    Serial.begin(9600);

    pinMode(U4_COM,OUTPUT);
    pinMode(U4_123,OUTPUT);
    pinMode(U4_456,OUTPUT);
    pinMode(U4_789,OUTPUT);

    pinMode(U1_COM,OUTPUT);
    pinMode(U1_1,OUTPUT);
    pinMode(U1_2,OUTPUT);
    pinMode(U1_3,OUTPUT);

    pinMode(U2_COM,OUTPUT);
    pinMode(U2_4,OUTPUT);
    pinMode(U2_5,OUTPUT);
    pinMode(U2_6,OUTPUT);

    pinMode(U3_COM,OUTPUT);
    pinMode(U3_7,OUTPUT);
    pinMode(U3_8,OUTPUT);
    pinMode(U3_9,OUTPUT);

    digitalWrite(U1_COM,HIGH);
    digitalWrite(U2_COM,HIGH);
    digitalWrite(U3_COM,HIGH);
    digitalWrite(U4_COM,HIGH);

    digitalWrite(U4_123,HIGH);
    digitalWrite(U4_456,LOW);
    digitalWrite(U4_789,LOW);

    digitalWrite(U1_1,HIGH);
    digitalWrite(U1_2,LOW);
    digitalWrite(U1_3,LOW);
 
    digitalWrite(U2_4,LOW);
    digitalWrite(U2_5,LOW);
    digitalWrite(U2_6,LOW);

    digitalWrite(U3_7,LOW);
    digitalWrite(U3_8,LOW);
    digitalWrite(U3_9,LOW);


  
  pixels.begin(); // INITIALIZE NeoPixel strip object (REQUIRED)

}





void loop() {

    

  pixels.clear(); // Set all pixel colors to 'off'
  analog = analogRead(A4);
  // The first NeoPixel in a strand is #0, second is 1, all the way up
  // to the count of pixels minus one.
  
  if(analog > 1024 - delta){
    delay(1);
    analog = analogRead(A4);
    if(analog > 1023 - delta){
       mode = 1;      
    }
  }
  if(analog > 836 - delta && analog < 836 + delta){
    delay(5);
    analog = analogRead(A4);
    if(analog > 836 - delta && analog < 836 + delta){
         mode = 2; 
    }
  }
  if(analog > 690 - delta && analog < 690 + delta){
     delay(5);
     analog = analogRead(A4);

    if(analog > 690 - delta && analog < 690 + delta){
      mode = 3;    
    }
  }

  if(analog > 569 - delta && analog < 569 + delta){
     delay(1);
     analog = analogRead(A4);

    if(analog > 569 - delta && analog < 569 + delta){
      mode = 4;    
    }
  }

  if(analog > 498 - delta && analog < 498 + delta){//buttons 4 and 6 at the same time with 2 fingers, like the three Stooges
     delay(1);
     analog = analogRead(A4);

    if(analog > 498 - delta && analog < 498 + delta){
      mode = -1;    
    }
  }

  if(analog > 464 - delta && analog < 464 + delta){
     delay(1);
     analog = analogRead(A4);

    if(analog > 464 - delta && analog < 464 + delta){
      mode = 5;    
    }
  }

  if(analog > 372 - delta && analog < 372 + delta){
     delay(1);
     analog = analogRead(A4);

    if(analog > 372 - delta && analog < 372 + delta){
      mode = 6;    
    }
  }

  if(analog > 283 - delta && analog < 283 + delta){
     delay(1);
     analog = analogRead(A4);

    if(analog > 283 - delta && analog < 283 + delta){
      mode = 7;    
    }
  }

  if(analog > 195 - delta && analog < 195 + delta){
     delay(1);
     analog = analogRead(A4);

    if(analog > 195 - delta && analog < 195 + delta){
      mode = 8;    
    }
  }

  if(analog > 103 - delta && analog < 103 + delta){
     delay(1);
     analog = analogRead(A4);

    if(analog > 103 - delta && analog < 103 + delta){
      mode = 9;    
    }
  }

  if (Serial.available()) {

    //read serial as ascii integer
     int ser = Serial.read();
    //    Serial.println(ser);
    if(ser == 48){    //ASCII for 0
      mode = 0;
     }  
     if(ser == 49){    //ASCII for 1
      mode = 1;
     }
     if(ser == 50){    //ASCII for 2
      mode = 2;
     }
     if(ser == 51){    //ASCII for 3
      mode = 3;
     }
     if(ser == 52){    //ASCII for 4
      mode = 4;
     }
     if(ser == 53){    //ASCII for 5
      mode = 5;
     }
     if(ser == 54){    //ASCII for 6
      mode = 6;
     }
     if(ser == 55){    //ASCII for 7
      mode = 7;
     }
     if(ser == 56){    //ASCII for 8
      mode = 8;
     }
     if(ser == 57){    //ASCII for 9
      mode = 9;
     }
     if(ser == 99){    //ASCII for c, which stands for "cycle"
      mode = -1;
     }

  }

  if(mode == 1){
    pixels.setPixelColor(0, pixels.Color(0, 0, 0));    
    pixels.setPixelColor(1, pixels.Color(0, 0, 0));    
    pixels.setPixelColor(2, pixels.Color(0, 0, 0));    
    pixels.setPixelColor(3, pixels.Color(0, 0, 0));    
    pixels.setPixelColor(4, pixels.Color(0, 0, 0));    
    pixels.setPixelColor(5, pixels.Color(0, 0, 0));    
    pixels.setPixelColor(6, pixels.Color(0, 0, 0));    
    pixels.setPixelColor(7, pixels.Color(0, 0, 0));    
    pixels.setPixelColor(8, pixels.Color(255, 0, 0));    

    digitalWrite(U4_123,HIGH);
    digitalWrite(U4_456,LOW);
    digitalWrite(U4_789,LOW);

    digitalWrite(U1_1,HIGH);
    digitalWrite(U1_2,LOW);
    digitalWrite(U1_3,LOW);
 
    digitalWrite(U2_4,LOW);
    digitalWrite(U2_5,LOW);
    digitalWrite(U2_6,LOW);

    digitalWrite(U3_7,LOW);
    digitalWrite(U3_8,LOW);
    digitalWrite(U3_9,LOW);

    
  }
  if(mode == 2){
    pixels.setPixelColor(0, pixels.Color(0, 0, 0));    
    pixels.setPixelColor(1, pixels.Color(0, 0, 0));    
    pixels.setPixelColor(2, pixels.Color(0, 0, 0));    
    pixels.setPixelColor(3, pixels.Color(0, 0, 0));    
    pixels.setPixelColor(4, pixels.Color(0, 0, 0));    
    pixels.setPixelColor(5, pixels.Color(0, 0, 0));    
    pixels.setPixelColor(6, pixels.Color(0, 0, 0));    
    pixels.setPixelColor(7, pixels.Color(255, 0, 0));    
    pixels.setPixelColor(8, pixels.Color(0, 0, 0));    
    
    digitalWrite(U4_123,HIGH);
    digitalWrite(U4_456,LOW);
    digitalWrite(U4_789,LOW);

    digitalWrite(U1_1,LOW);
    digitalWrite(U1_2,HIGH);
    digitalWrite(U1_3,LOW);
 
    digitalWrite(U2_4,LOW);
    digitalWrite(U2_5,LOW);
    digitalWrite(U2_6,LOW);

    digitalWrite(U3_7,LOW);
    digitalWrite(U3_8,LOW);
    digitalWrite(U3_9,LOW);
 
  }
  if(mode == 3){
    pixels.setPixelColor(0, pixels.Color(0, 0, 0));    
    pixels.setPixelColor(1, pixels.Color(0, 0, 0));    
    pixels.setPixelColor(2, pixels.Color(0, 0, 0));    
    pixels.setPixelColor(3, pixels.Color(0, 0, 0));    
    pixels.setPixelColor(4, pixels.Color(0, 0, 0));    
    pixels.setPixelColor(5, pixels.Color(0, 0, 0));    
    pixels.setPixelColor(6, pixels.Color(255, 0, 0));    
    pixels.setPixelColor(7, pixels.Color(0, 0, 0));    
    pixels.setPixelColor(8, pixels.Color(0, 0, 0));    
    
    digitalWrite(U4_123,HIGH);
    digitalWrite(U4_456,LOW);
    digitalWrite(U4_789,LOW);

    digitalWrite(U1_1,LOW);
    digitalWrite(U1_2,LOW);
    digitalWrite(U1_3,HIGH);
 
    digitalWrite(U2_4,LOW);
    digitalWrite(U2_5,LOW);
    digitalWrite(U2_6,LOW);

    digitalWrite(U3_7,LOW);
    digitalWrite(U3_8,LOW);
    digitalWrite(U3_9,LOW);    

  }
  if(mode == 4){
    pixels.setPixelColor(0, pixels.Color(0, 0, 0));    
    pixels.setPixelColor(1, pixels.Color(0, 0, 0));    
    pixels.setPixelColor(2, pixels.Color(0, 0, 0));    
    pixels.setPixelColor(3, pixels.Color(0, 0, 0));    
    pixels.setPixelColor(4, pixels.Color(0, 0, 0));    
    pixels.setPixelColor(5, pixels.Color(255, 0, 0));    
    pixels.setPixelColor(6, pixels.Color(0, 0, 0));    
    pixels.setPixelColor(7, pixels.Color(0, 0, 0));    
    pixels.setPixelColor(8, pixels.Color(0, 0, 0));    
    
    digitalWrite(U4_123,LOW);
    digitalWrite(U4_456,HIGH);
    digitalWrite(U4_789,LOW);

    digitalWrite(U1_1,LOW);
    digitalWrite(U1_2,LOW);
    digitalWrite(U1_3,LOW);
 
    digitalWrite(U2_4,HIGH);
    digitalWrite(U2_5,LOW);
    digitalWrite(U2_6,LOW);

    digitalWrite(U3_7,LOW);
    digitalWrite(U3_8,LOW);
    digitalWrite(U3_9,LOW);    


  }
  if(mode == 5){
    pixels.setPixelColor(0, pixels.Color(0, 0, 0));    
    pixels.setPixelColor(1, pixels.Color(0, 0, 0));    
    pixels.setPixelColor(2, pixels.Color(0, 0, 0));    
    pixels.setPixelColor(3, pixels.Color(0, 0, 0));    
    pixels.setPixelColor(4, pixels.Color(255, 0, 0));    
    pixels.setPixelColor(5, pixels.Color(0, 0, 0));    
    pixels.setPixelColor(6, pixels.Color(0, 0, 0));    
    pixels.setPixelColor(7, pixels.Color(0, 0, 0));    
    pixels.setPixelColor(8, pixels.Color(0, 0, 0));    

    digitalWrite(U4_123,LOW);
    digitalWrite(U4_456,HIGH);
    digitalWrite(U4_789,LOW);

    digitalWrite(U1_1,LOW);
    digitalWrite(U1_2,LOW);
    digitalWrite(U1_3,LOW);
 
    digitalWrite(U2_4,LOW);
    digitalWrite(U2_5,HIGH);
    digitalWrite(U2_6,LOW);

    digitalWrite(U3_7,LOW);
    digitalWrite(U3_8,LOW);
    digitalWrite(U3_9,LOW);    


  }
  if(mode == 6){
    pixels.setPixelColor(0, pixels.Color(0, 0, 0));    
    pixels.setPixelColor(1, pixels.Color(0, 0, 0));    
    pixels.setPixelColor(2, pixels.Color(0, 0, 0));    
    pixels.setPixelColor(3, pixels.Color(255, 0, 0));    
    pixels.setPixelColor(4, pixels.Color(0, 0, 0));    
    pixels.setPixelColor(5, pixels.Color(0, 0, 0));    
    pixels.setPixelColor(6, pixels.Color(0, 0, 0));    
    pixels.setPixelColor(7, pixels.Color(0, 0, 0));    
    pixels.setPixelColor(8, pixels.Color(0, 0, 0));    

    digitalWrite(U4_123,LOW);
    digitalWrite(U4_456,HIGH);
    digitalWrite(U4_789,LOW);

    digitalWrite(U1_1,LOW);
    digitalWrite(U1_2,LOW);
    digitalWrite(U1_3,LOW);
 
    digitalWrite(U2_4,LOW);
    digitalWrite(U2_5,LOW);
    digitalWrite(U2_6,HIGH);

    digitalWrite(U3_7,LOW);
    digitalWrite(U3_8,LOW);
    digitalWrite(U3_9,LOW);

  }

  if(mode == 7){
    pixels.setPixelColor(0, pixels.Color(0, 0, 0));    
    pixels.setPixelColor(1, pixels.Color(0, 0, 0));    
    pixels.setPixelColor(2, pixels.Color(255, 0, 0));    
    pixels.setPixelColor(3, pixels.Color(0, 0, 0));    
    pixels.setPixelColor(4, pixels.Color(0, 0, 0));    
    pixels.setPixelColor(5, pixels.Color(0, 0, 0));    
    pixels.setPixelColor(6, pixels.Color(0, 0, 0));    
    pixels.setPixelColor(7, pixels.Color(0, 0, 0));    
    pixels.setPixelColor(8, pixels.Color(0, 0, 0));    

    digitalWrite(U4_123,LOW);
    digitalWrite(U4_456,LOW);
    digitalWrite(U4_789,HIGH);

    digitalWrite(U1_1,LOW);
    digitalWrite(U1_2,LOW);
    digitalWrite(U1_3,LOW);
 
    digitalWrite(U2_4,LOW);
    digitalWrite(U2_5,LOW);
    digitalWrite(U2_6,LOW);

    digitalWrite(U3_7,HIGH);
    digitalWrite(U3_8,LOW);
    digitalWrite(U3_9,LOW);

 }
  if(mode == 8){
    pixels.setPixelColor(0, pixels.Color(0, 0, 0));    
    pixels.setPixelColor(1, pixels.Color(255, 0, 0));    
    pixels.setPixelColor(2, pixels.Color(0, 0, 0));    
    pixels.setPixelColor(3, pixels.Color(0, 0, 0));    
    pixels.setPixelColor(4, pixels.Color(0, 0, 0));    
    pixels.setPixelColor(5, pixels.Color(0, 0, 0));    
    pixels.setPixelColor(6, pixels.Color(0, 0, 0));    
    pixels.setPixelColor(7, pixels.Color(0, 0, 0));    
    pixels.setPixelColor(8, pixels.Color(0, 0, 0));    

    digitalWrite(U4_123,LOW);
    digitalWrite(U4_456,LOW);
    digitalWrite(U4_789,HIGH);
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

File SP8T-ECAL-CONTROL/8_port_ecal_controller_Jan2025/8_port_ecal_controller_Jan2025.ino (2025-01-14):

#include <Adafruit_NeoPixel.h>
#ifdef __AVR__
#endif

// Which pin on the Arduino is connected to the NeoPixels?
#define PIN 59 //59 on the Mega. the Mega must be used for this mode of operation, as the UNO lacks the required number of output pins

// How many NeoPixels are attached to the Arduino?
#define NUMPIXELS 12 // 8 switch positions for SP8T plus 4 positions for short, open, load and thru

// When setting up the NeoPixel library, we tell it how many pixels,  
// and which pin to use to send signals. Note that for older NeoPixel
// strips you might need to change the third parameter -- see the
// strandtest example for more information on possible values.
Adafruit_NeoPixel pixels(NUMPIXELS, PIN, NEO_GRB + NEO_KHZ800);


//the Arduino pins which mapt to the various switch states in the "level 2" switches
#define SP8T_1 3
#define SP8T_2 7
#define SP8T_3 6
#define SP8T_4 2
#define SP8T_5 8
#define SP8T_6 4
#define SP8T_7 5
#define SP8T_8 9

//arduino pins which map to the control lines for the "level 3" isolation switches
#define NOT_SP8T_1 54 //UNO pin 14, A0
#define NOT_SP8T_2 55 //UNO pin 15, A1
#define NOT_SP8T_3 10
#define NOT_SP8T_4 11
#define NOT_SP8T_5 12
#define NOT_SP8T_6 13
#define NOT_SP8T_7 56 //UNO pin 16, A2
#define NOT_SP8T_8 57 //UNO pin 17, A3

//pins from the Arduino MEGA which control the positions of the "level 1" switch
#define ECAL_SHORT 34
#define ECAL_LOAD 36
#define ECAL_1234 32
#define ECAL_5678 30

int analog = 0;// analog state variable of the button analog control line for the 1-8 switch state buttons, read from Analog pin A8
int analogEcal = 0;// analog state variable of the button analog control line for the E-cal, read from analog pin A4
int delta = 20;
int mode = 1;//modes are 1,2,3,4,5,6,7,8 which are pixel 7,6,5,4,3,2,1, and 0 respectively
int modeEcal = 4;//modes are 1,2,3,4 which are pixel 3,2,1, and 0 respectively. mode 1 is short, 2 is open, 3 is load, 4 is thru


void setup() {
    Serial.begin(9600);


    pinMode(SP8T_1,OUTPUT);
    pinMode(SP8T_2,OUTPUT);
    pinMode(SP8T_3,OUTPUT);
    pinMode(SP8T_4,OUTPUT);
    pinMode(SP8T_5,OUTPUT);
    pinMode(SP8T_6,OUTPUT);
    pinMode(SP8T_7,OUTPUT);
    pinMode(SP8T_8,OUTPUT);

    pinMode(NOT_SP8T_1,OUTPUT);
    pinMode(NOT_SP8T_2,OUTPUT);
    pinMode(NOT_SP8T_3,OUTPUT);
    pinMode(NOT_SP8T_4,OUTPUT);
    pinMode(NOT_SP8T_5,OUTPUT);
    pinMode(NOT_SP8T_6,OUTPUT);
    pinMode(NOT_SP8T_7,OUTPUT);
    pinMode(NOT_SP8T_8,OUTPUT);

    pinMode(ECAL_SHORT,OUTPUT);
    pinMode(ECAL_LOAD,OUTPUT);
    pinMode(ECAL_1234,OUTPUT);
    pinMode(ECAL_5678,OUTPUT);

    digitalWrite(SP8T_1,LOW);
    digitalWrite(SP8T_2,LOW);
    digitalWrite(SP8T_3,LOW);
    digitalWrite(SP8T_4,LOW);
    digitalWrite(SP8T_5,LOW);
    digitalWrite(SP8T_6,LOW);
    digitalWrite(SP8T_7,LOW);
    digitalWrite(SP8T_8,LOW);
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

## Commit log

2024-08-03 put most files into the repo in folders
    [6button-6eopixel.SchDoc, 6button-6neopixel.PcbDoc, 6button-6neopixels.PrjPcb, 8button-8eopixel.SchDoc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]
2024-08-05 adding bud box documentation
    [9button-9neopixel.PcbDoc, 9button-9neopixel.SLDDRW, 9button-9neopixel.SLDPRT, 9button-9neopixel.SchDoc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]
2024-08-05 many images of assembly process
2024-08-08 adding arduino code
2024-08-08 added a bunch of machining files
    [HBracket-M4.SLDDRW, HBracket-M4.SLDPRT, center-block-outside.SLDDRW, center-block-outside.SLDPRT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]
2024-08-08 improving arduino code
2024-08-08 added CAD for wood panel, stared a BOM spreadsheet
    [BOM.xlsx, rack-mount-board.SLDDRW, rack-mount-board.SLDPRT]
2024-08-08 many images from phone of assembly
    [BOM.xlsx]
2024-08-09 added drawing for 3d printed arduino bracket
    [arduino-bracket.SLDDRW]
2024-08-09 images and powerpoints
2024-08-11 added more documentation to arduino build and added a system build powerpoint
2024-08-11 Update System Assembly.pptx
2024-08-12 build documentation
    [92700A103_Male-Female Threaded Hex Standoff(1).SLDPRT, 92700A466_Male-Female Threaded Hex Standoff(1).SLDPRT]
2024-08-12 build docs
    [92700A103_Male-Female Threaded Hex Standoff(1).SLDPRT, 92700A466_Male-Female Threaded Hex Standoff(1).SLDPRT, 93465A106_Brass Socket Head Screw.SLDPRT, cold-as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]
2024-08-13 BOM updates
    [BOM.xlsx]
2024-08-13 tweaking file names
    [AN-1304-A-box-modifications.SLDDRW, AN-1304-A-box-modifications.SLDPRT, AN-1304-A-box-modifications.STEP, AN-1304-A-lid-machined.SLDDRW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]
2024-08-13 improving structure of documentation
    [AN-1304-A-box-modifications.SLDDRW, BOM.xlsx, H-Bracket.SLDDRW, H-Bracket.SLDPRT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]
2024-08-13 build documentation improvement
    [BOM.xlsx]
2024-08-14 custom metal box docs
    [BOM.xlsx]
2024-08-14 circuit board assembly document
2024-08-15 tons of documentation work
    [AN-1304-A-box-modifications.SLDDRW, BOM.xlsx, DB25-relay-HV-control.PrjPcb, DB25-relay-HV-control.SchDoc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]
2024-08-16 small improvements to PCB docs
2024-08-17 adding RF pcb's
    [10cm-chip-cal-board-1point2in.PcbDoc, 10cm-chip-cal-board-1point2in.step, 6button-6neopixel.step, 6button-6neopixels.PrjPcb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]
2024-08-17 pcb file work
    [6button-6neopixel.step.SLDDRW, 6button-6neopixel.step.SLDPRT, 8button-8neopixel.SLDDRW, 8button-8neopixel.SLDPRT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]
2024-08-18 big build with all the builds together
    [rectangle11board-BOM.xlsx, rectangle11board.SLDDRW, rectangle11board.SLDPRT]
2024-08-20 drawing update on cal board
    [thru-cal-board-1point2in.step.SLDDRW]
2024-08-20 more images and drawings
    [load-cal-board-1point2in.SLDDRW, load-cal-board-1point2in.SLDPRT, load-cal-board-1point2in.step]
2024-08-26 readme updates and making better names of files
    [cal-boards-panelixation1-BOM-edited.xlsx, cal-boards-panelization1-bom.xlsx]
2024-08-26 added numerous dimensioned drawings
    [HV-DCDC-bracket.SLDDRW, arduino-bracket.SLDDRW, front-panel-center-bracket.SLDDRW, front-panel-edge-bracket.SLDDRW]
2024-08-29 redesigned 6 pixel board to have correct hole dimensions
    [6button-6neopixel.GBL, 6button-6neopixel.GBO, 6button-6neopixel.GBP, 6button-6neopixel.GBS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]
2024-08-30 many updates to the SP6T system documentation
    [171-025-203.SLDPRT, 171-025-203.STEP, 6button-6neopixel.PcbDoc, 6button-6neopixel.SLDDRW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]
2024-08-30 made a separate pdf for just the template cutout for the SP6T wood board
2024-08-30 rack mount board design
    [rack-mount-board-SP6T.SLDDRW, rack-mount-board-SP6T.SLDPRT, rack-mount-board.SLDDRW, rack-mount-board.SLDPRT]
2024-09-16 fixed pin mapping on sp8t +ecal control in arduino code
2024-09-16 added sp8t files
    [NC_Menlo Micro SP8T RF Board_04212024.SLDASM, NC_Menlo Micro SP8T RF Board_04212024.SLDDRW, NC_Menlo Micro SP8T RF Board_04212024.step, SP8T_nistmods.PrjPcb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]
2024-09-18 pluto bracket change
    [arduino-bracket.SLDDRW, pluto-bracket-base.SLDPRT]
2024-09-18 drastic simplification of overall structure of repository
    [10cm-chip-cal-board-1point2in.PcbDoc, 10cm-chip-cal-board-1point2in.step, 171-025-203.SLDPRT, 171-025-203.STEP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]
2024-09-18 removed a bunch of files which are not part of core set of files
    [6button-6neopixel.GBL, 6button-6neopixel.GBO, 6button-6neopixel.GBP, 6button-6neopixel.GBS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]
2024-09-18 added links to all the files for SP8T_ecal
    [SP8T_ecal.PrjPcb, SP8T_ecal_1.SchDoc, SP8T_ecal_2.SchDoc, SP8T_ecal_3.SchDoc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]
2024-09-23 improved the sp6t layout template, readme flow, bom
    [BOM.xlsx, rack-mount-board-SP6T.SLDDRW]
2024-10-13 some little improvements
    [BOM.xlsx, DB25-relay-HV-control.PcbDoc, DB25-relay-HV-control.PrjPcb]
2024-10-21 update all the files for #6 wood screws and press fit inserts, and add bracket for cryoelec board
    [arduino-bracket-v2.SLDPRT, arduino-bracket-v2.STL, cryoelec-bracket.SLDDRW, cryoelec-bracket.SLDPRT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]
2024-10-24 made a jupyter control notebook for sp8t, added better sequence to arduino for sp8t
2024-10-24 rotated bracket for cryoelec
    [cryoelec-bracket-rotated.SLDDRW, cryoelec-bracket-rotated.SLDPRT, cryoelec-bracket-rotated.STL]
2024-10-30 wood board updates
    [rack-mount-board-SP9T.SLDDRW, rack-mount-board-SP9T.SLDPRT]
2024-10-30 changed diameter of hole for 4-40 thread inserts in arduino bracket
    [arduino-bracket-v2.SLDDRW, arduino-bracket-v2.SLDPRT, arduino-bracket-v2.STL]
2024-10-30 update to overly large holes for all the thread inserts to test them out
    [cryoelec-bracket-rotated.SLDDRW, cryoelec-bracket-rotated.SLDPRT, cryoelec-bracket-rotated.STL, front-panel-edge-bracket-v2.SLDDRW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]
2024-10-30 wood all updated with better hole size markings on templates
    [rack-mount-board-SP6T.SLDDRW, rack-mount-board-SP9T.SLDDRW]
2024-10-30 reorg into a final publication format, built out the README for 3d print files specifically
    [arduino-bracket-v2.SLDDRW, arduino-bracket-v2.SLDPRT, arduino-bracket-v2.STL, arduino-bracket.SLDDRW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]
2024-10-31 metal box is now a set separate from "machining"
    [AN-1304-A-box-modifications.SLDDRW, AN-1304-A-box-modifications.SLDPRT, AN-1304-A-box-modifications.STEP, AN-1304-A-lid-modifications.SLDDRW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]
2024-10-31 condensing the set of pcb files to be only room temperature, and only the 2 builds
    [8button-8eopixel.SchDoc, 8button-8neopixel.PcbDoc, 8button-8neopixel.SLDDRW, 8button-8neopixel.SLDPRT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]
2024-10-31 lots of updates on structure of pcb files
    [6button-6neopixel-BOM.xlsx, 6button-6neopixels.PrjPcb, 9button-9neopixel-BOM.xlsx, DB25-relay-HV-control-BOM.xlsx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]
2024-11-01 moved code into code directory, cleand up some files, updated BOM for 6 pole build
    [Fiducial.PcbLib, Fiducial.SchLib, MM5130_FOOTPRINT.PcbLib, MM5130_SCHSYM.SCHLIB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]
2024-11-02 build file list tool in javascript and PHP in PCB folder
    [files.csv]
2024-11-02 files.html updates
    [files.csv]
2024-11-02 put all the files together in the main folder of the repository
    [6button-6eopixel.SchDoc, 6button-6neopixel-BOM.xlsx, 6button-6neopixel.PcbDoc, 6button-6neopixels.PrjPcb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]
2024-11-03 working on going from excel to csv to markdown in code
    [SP9T-Custom-System-Build-BOM-old.xlsx, SP9T-Custom-System-Build-BOM.csv, SP9T-Custom-System-Build-BOM.xlsx]
2024-11-03 totally re-arranged the structure of the repository
    [10cm-chip-cal-board-1point2in.PcbDoc, 10cm-chip-cal-board-1point2in.step, 171-025-203.SLDPRT, 171-025-203.STEP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]
2024-11-05 fixed annotations of dimensions in machine drawing of metal box lid
    [AN-1304-A-lid-modifications.SLDDRW]
2024-11-05 update drawings again
    [AN-1304-A-box-modifications.SLDDRW]
2024-11-26 update sp3t
    [cryoelec-bracket-SP3T.SLDDRW, cryoelec-bracket-SP3T.SLDPRT, cryoelec-bracket-SP3T.STL]
2024-11-26 sp3t work
    [cryoelec-bracket-SP3T.SLDDRW, cryoelec-bracket-SP3T.SLDPRT, cryoelec-bracket-SP3T.STL]
2024-11-26 update readme with drawing and link to new 3d print file
2024-11-26 adding 24 line generic controller to MEMSduino
    [24line-control-panel.PcbDoc, 24line-control-panel.PrjPcb, 24line-control-panel.SchDoc, DB25-relay-HV-control.PcbDoc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]
2024-11-26 much documentation added
    [24line-DB25-relay-HV-control.PcbDoc, 24line-DB25-relay-HV-control.PrjPcb, 24line-arduino-to-headers-shield.PcbDoc, 24line-control-panel.PcbDoc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]
2024-11-27 3D printed part and poster updates for SP3T
2024-11-28 arduino control
2025-01-14 sp8t arduino code added with updates
2025-01-28 sp9t work
    [microd-header-adapter-board-rev2.PcbDoc, microd-header-adapter-board-rev2.PrjPcb, microd-header-adapter-board-rev2.SchDoc, microd-header-adapter-board-rev2.step]
2025-02-07 documenting dual SP3T version 2
    [cryoelec-bracket-SP3T.SLDDRW, cryoelec-bracket-SP3T.SLDPRT, cryoelec-bracket-SP3T.STL, switch_logic.xlsx]
2025-02-10 dual sp3d updates and gif added to readme
    [cryoelec-bracket-SP3T.SLDDRW, cryoelec-bracket-SP3T.SLDPRT, cryoelec-bracket-SP3T.STL, rack-mount-board-SP6T.SLDDRW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]
2025-02-24 prototype design of zero fasteners arduino bracket
    [arduino-bracket-noscrews.SLDPRT, arduino-bracket-noscrews.STL]
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
